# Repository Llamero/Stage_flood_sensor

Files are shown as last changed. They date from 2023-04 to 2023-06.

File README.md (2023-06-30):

# Stage Flood Sensor

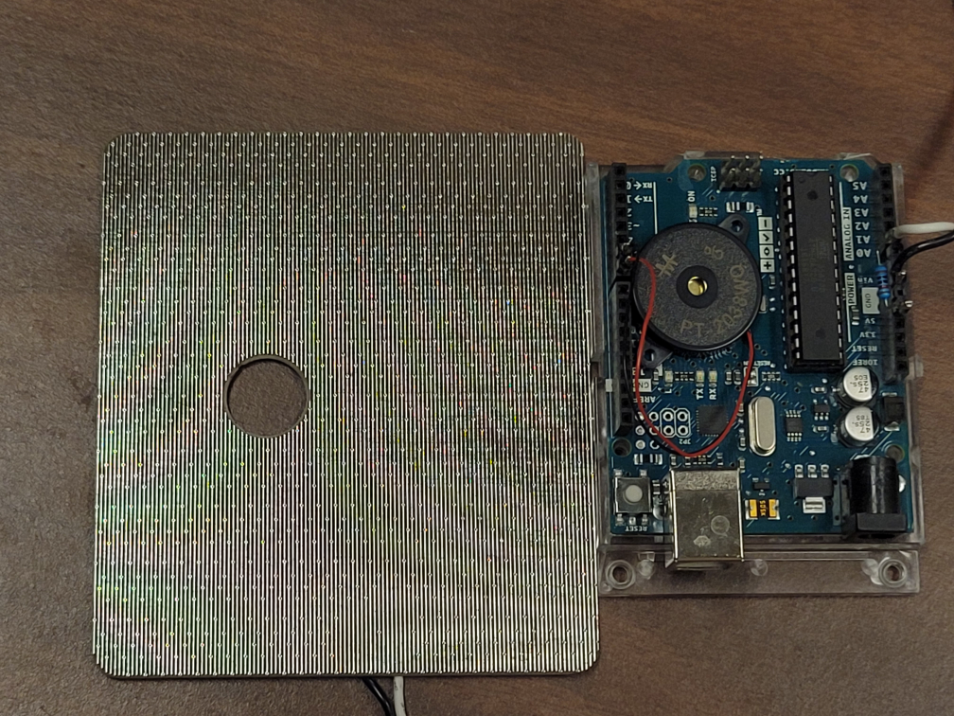
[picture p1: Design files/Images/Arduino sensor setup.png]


## Summary:

This is an open-source liquid sensor for microscopes.  It works by measuring the resistance between pairs of conductors separated by 550 µm.
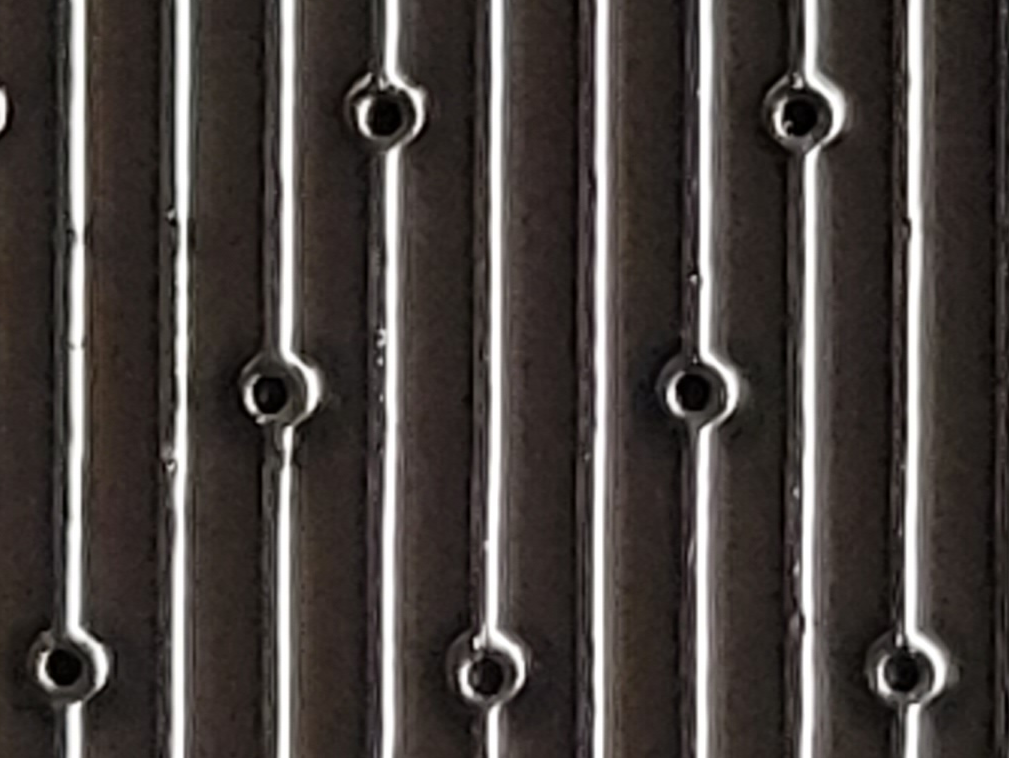
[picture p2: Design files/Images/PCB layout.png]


The four-layer layout with a grid of vias connecting to the layers allows for the the sensor board to be cut and shaped as needed without interfering with the electrical connections.  

## Installation (Arduino Uno):

1) Order the sensor PCB by uploading the provided Gerber files to a PCB manufacturer such as [OSH Park](https://oshpark.com/), [PCBWay](https://www.pcbway.com/orderonline.aspx), [Ailser](https://aisler.net/), etc.
2) If using an Arduino, order the following items:
- [Arduino Uno](https://www.digikey.com/en/products/detail/arduino/A000066/2784006)
- [Piezo transducer](https://www.digikey.com/en/products/detail/mallory-sonalert-products-inc/PT-2038WQ/1957869)
- [10 kOhm throughhole resistor](https://www.digikey.com/en/products/detail/stackpole-electronics-inc/CF14JT10K0/1741265)
- [Header pins](https://www.digikey.com/en/products/detail/w%C3%BCrth-elektronik/61300811121/4846839)
- Wires and solder
- Note: If using the [High-Speed Programmable LED Driver](https://github.com/Llamero/Four_Channel_MHz_LED_Driver), the sensor can connect directly to the external thermistor port, so only wire and solder is needed.
3) Cut/drill the sensor PCB as needed
4) Solder across both jumpers if an RC filter isn't used, otherwise solder on the desired resistor and capacitor combination.
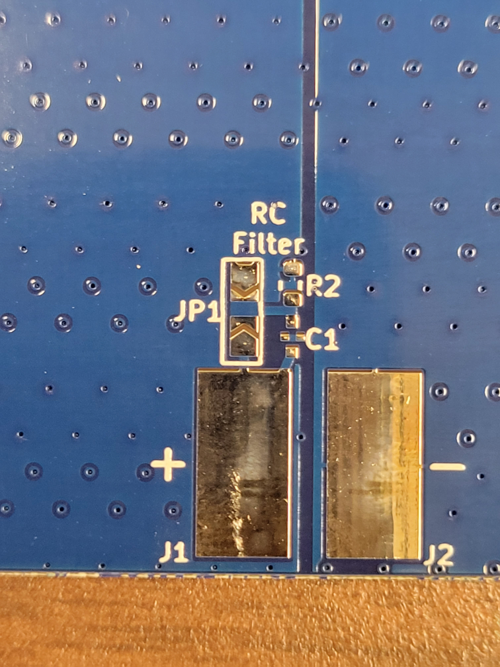
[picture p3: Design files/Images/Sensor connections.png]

5) Solder a pair of wires to the two wire pads.
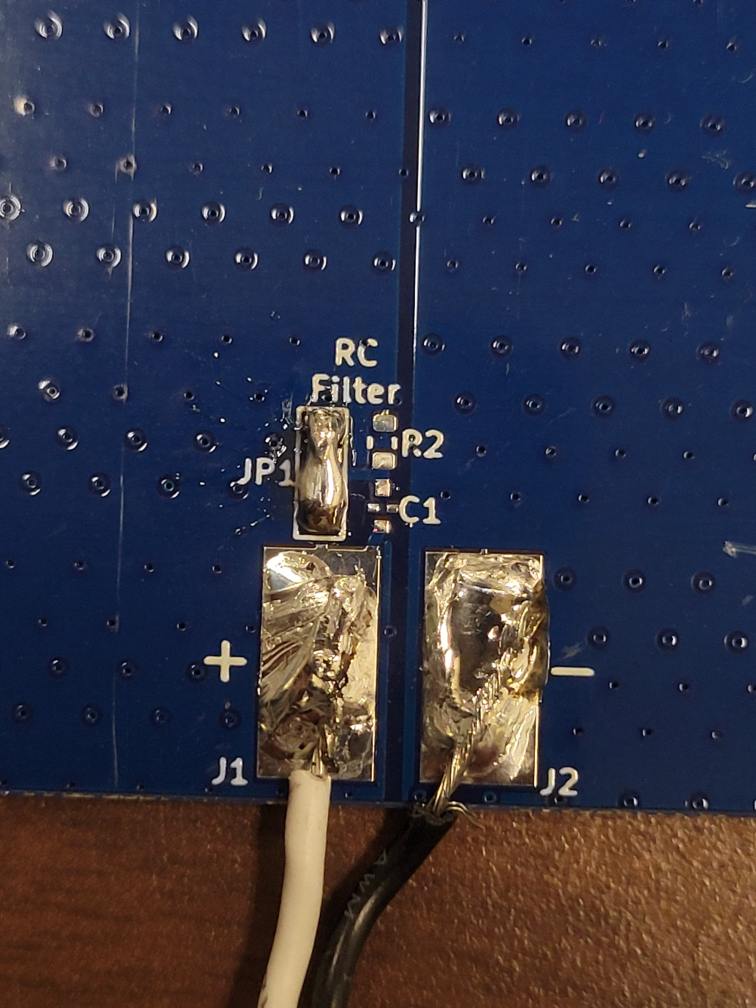
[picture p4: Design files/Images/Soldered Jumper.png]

6) Cut a set of 5 pins from the header pins.
7) Solder the 10 kOhm resistor between the 5V pin and A0 pin on the arduino.
8) Solder the positive wire to pin A0.
9) Solder the negative wire to GND.

10) Cut a pair of pins from the header pins.
11) Solder the two piezo wires to the pins (polarity does not matter).
12) Insert the pins to digital pins 6 and 7.
13) Upload the provided code to the Arduino.

## Installation (LED Driver):

1) Follow steps 1-5 for the Arduino Uno installation
2) Connect the wires to the "External Therm" port on the LED driver.
3) Set the "External Fault" temperature to 0° and the "External Warn" temperature to 1°C.  For higher sensitivity, also increase the "Resistance at 25°C" value.  For example, a value of 90000 will allow the sensor to detect deionized water.

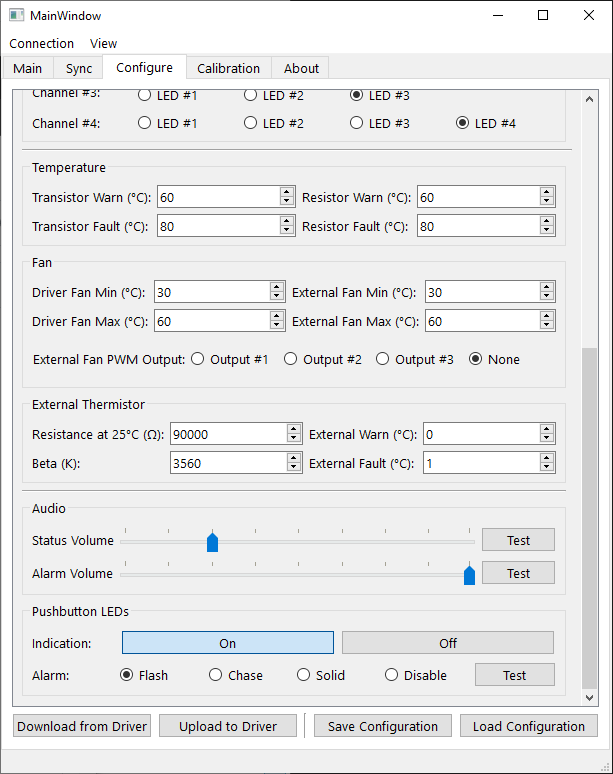
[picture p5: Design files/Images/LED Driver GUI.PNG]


## Troubleshooting 

Test the driver by applying a drop of water or PBS onto the sensor.  This should trip the alarm and wiping the liquid off should reset the alarm:
- [Arduino alarm example](https://www.youtube.com/watch?v=3DOJQmaSFc4&ab_channel=BenjaminESmith)
- [LED driver example](https://www.youtube.com/watch?v=jpRJdUz0464&ab_channel=BenjaminESmith)

If the alarm trips without liquid, this means there is a short on the board.  If the board was cut or drilled, then sand these regions and inspect the board under a microscope for any shorting traces.

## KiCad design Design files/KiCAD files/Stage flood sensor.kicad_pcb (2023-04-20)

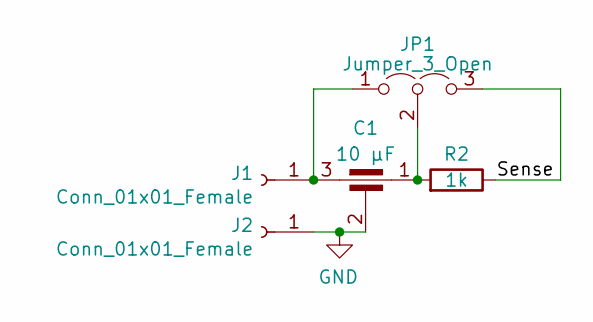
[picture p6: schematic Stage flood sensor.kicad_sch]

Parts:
C1: 10 µF; 0603 Passthrough capacitor; Part # YFF18PH0J106MT00HE
J1, J2: Conn_01x01_Female; SolderWirePad_1x01_SMD_5x10mm
JP1: Jumper_3_Open; SolderJumper-3_P2.0mm_Open_TrianglePad1.0x1.5mm_NumberLabels
R2: 1k; R_0603_1608Metric; Part # RNCP0603FTD1K00

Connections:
/Sense: JP1.3 (B), R2.1
GND: C1.2, J2.1
unnamed: C1.3, J1.1, JP1.1 (A)
unnamed: C1.1, JP1.2 (C), R2.2

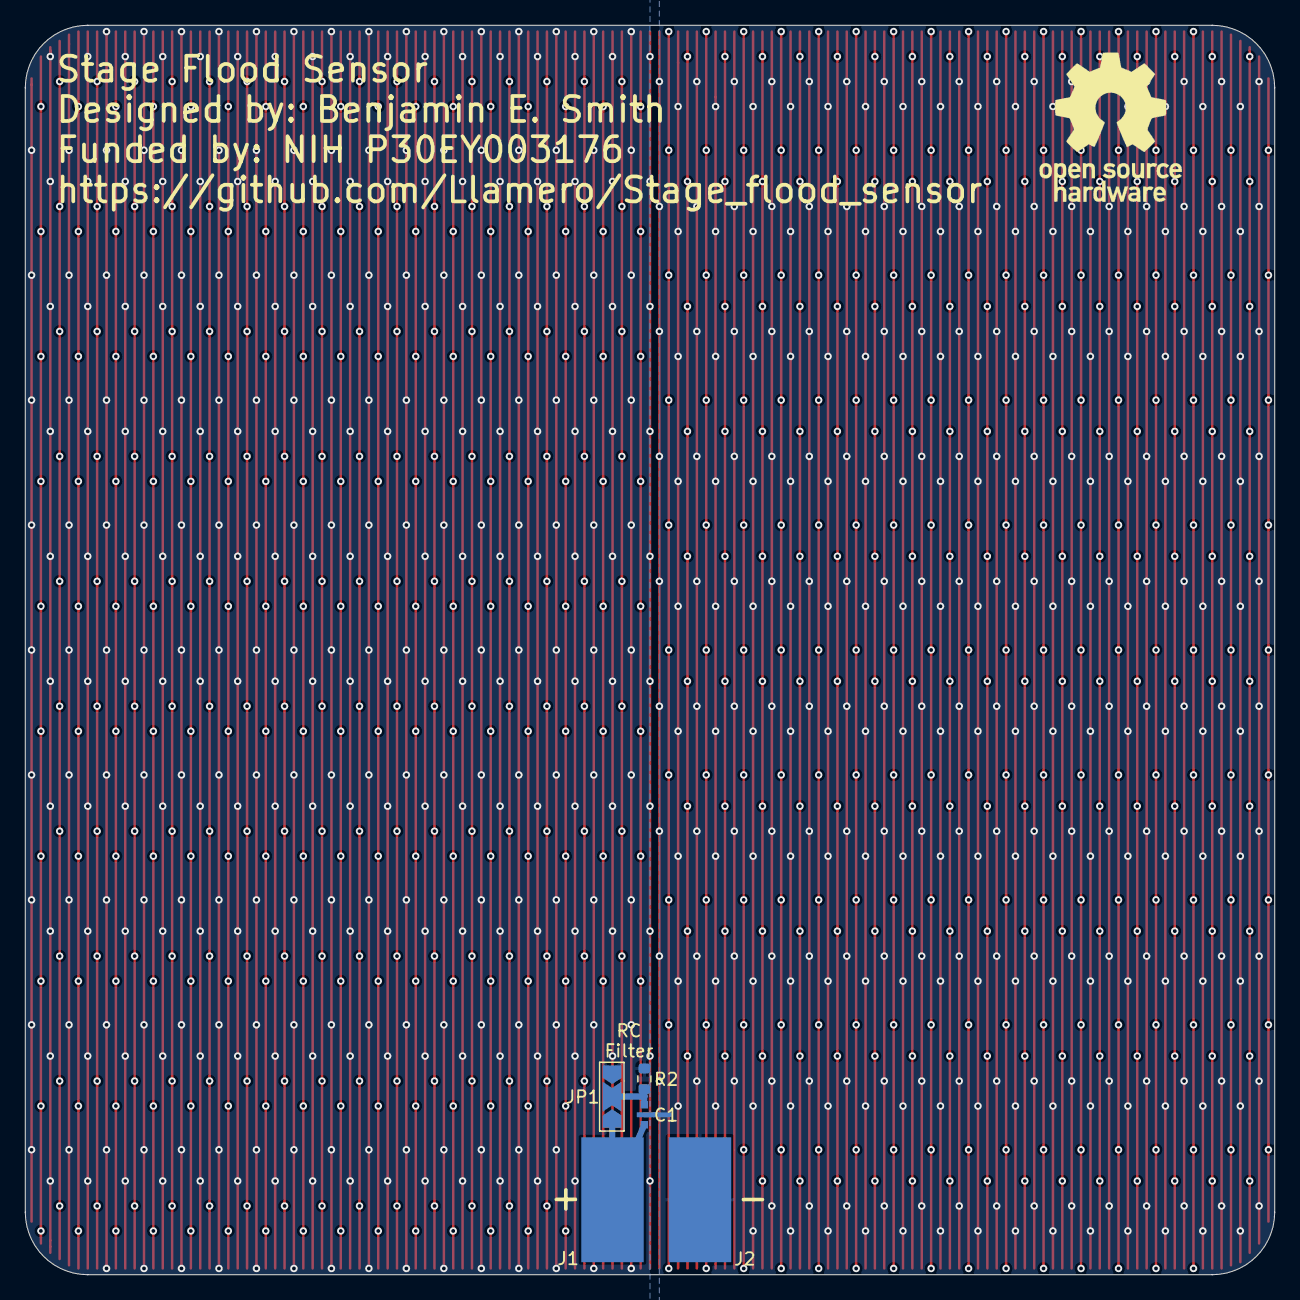
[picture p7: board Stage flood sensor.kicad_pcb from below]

Board: 4 copper layers, 100.0 x 100.0 mm, 5 parts (5 on the bottom side), 4 nets.

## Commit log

2023-05-06 Add Arduino code
2023-05-06 Organize directories
    [Stage flood sensor - Dual resolution.kicad_pcb, Stage flood sensor-B_Cu.gbl, Stage flood sensor-B_Mask.gbs, Stage flood sensor-B_Paste.gbp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]
